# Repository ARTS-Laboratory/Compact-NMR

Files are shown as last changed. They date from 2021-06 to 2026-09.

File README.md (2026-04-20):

# Compact-NMR (cNMR)

A compact Time-Domain Nuclear Magnetic Resonance (TD-NMR) system. The system is made up of custom NMR electronics with a compact and rugged permanent magnet array designed to enable future deployment as an in situ sensor. A signal-to-noise ratio of 25 dB has been demonstrated for a single scan, and sufficient data can be acquired in one minute for Time-Domain measurements. A high-level overview of the system is presented in Figures 1-5. For more details related to its potential use, refer to references [1] and [2]. 

<p align="center">
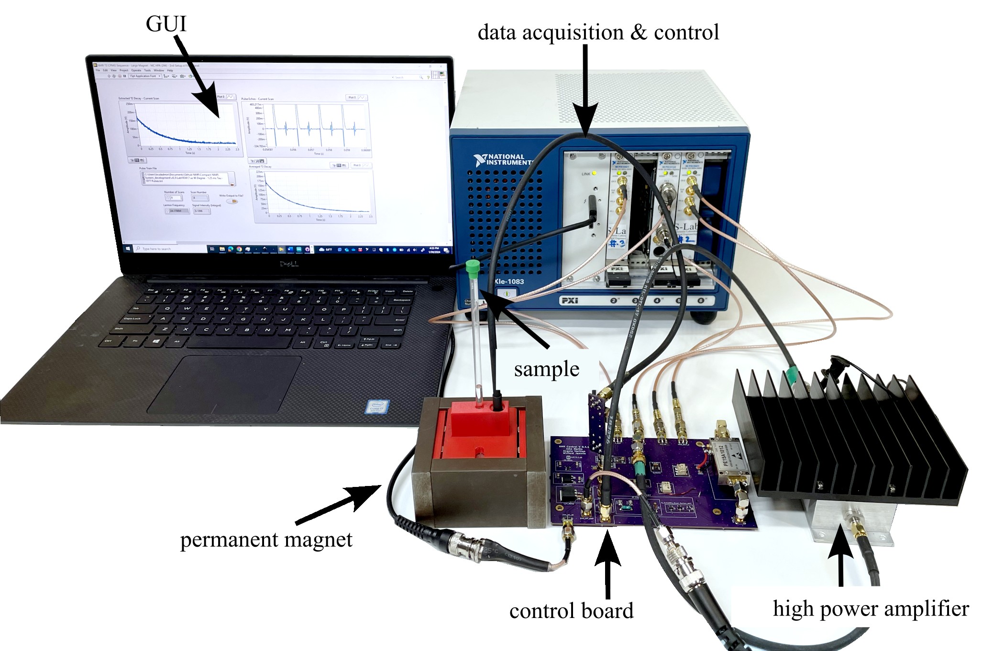
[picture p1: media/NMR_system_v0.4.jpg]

</p>
<p align="center">
Figure 1: Full setup for the TD-NMR system, with key components and subsystems annotated. 
</p>

<p align="center">
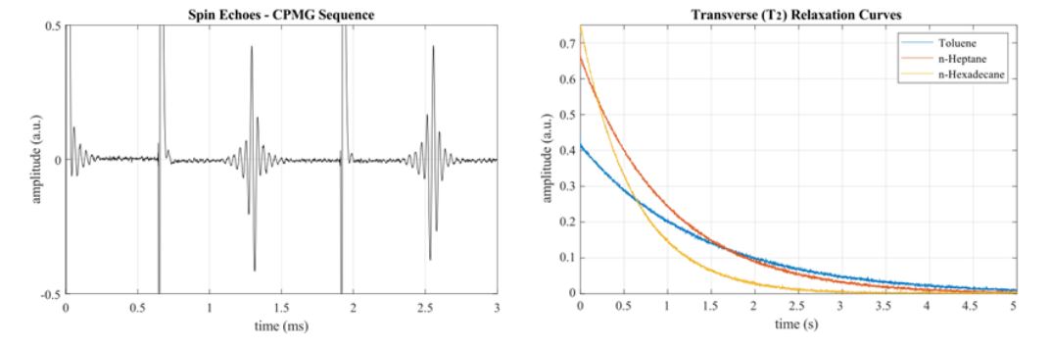
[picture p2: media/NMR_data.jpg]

</p>
<p align="center">
Figure 2: Data Obtained From the Nmr System Showing: (Left) Toluene Spin Echos Resulting From the Application of One 90◦ Pulse and Two 180◦ Pulses, and; (Right) T2 Relaxation Curves for Toluene, Heptane, and Hexadecane Following 32 Averages of 3965 Spin Echo Pulses.  
</p>

<p align="center">
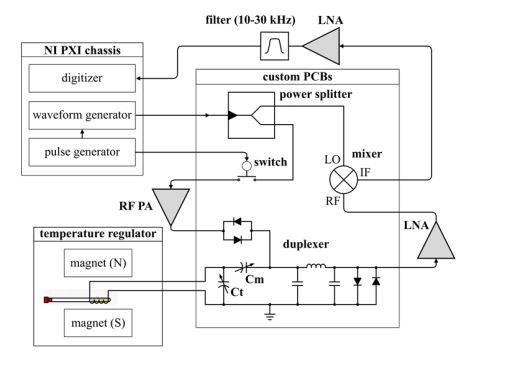
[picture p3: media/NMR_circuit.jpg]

</p>
<p align="center">
Figure 3: Full Schematic of the Control System, Permanent Magnet, and Signal Routing and Amplification Electronics for the Compact Td-nmr System.
</p>

<p align="center">
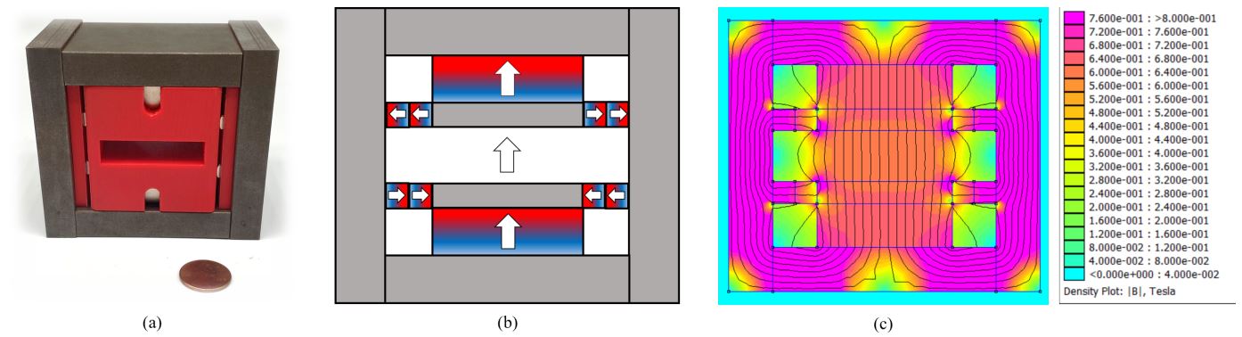
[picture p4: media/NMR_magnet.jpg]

</p>
<p align="center">
Figure 4: The magnet array, showing: (a) fully assembled magnet; (b) orientation of individual magnets and steel pieces, and; (c) two-dimensional finite element simulation.
</p>

<p align="center">
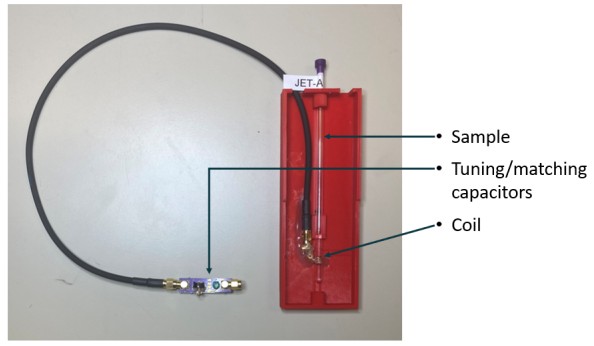
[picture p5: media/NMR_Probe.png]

</p>
<p align="center">
Figure 5: NMR probe with key components annotated. 
</p>

### References
[1] Jacob S. Martin, Austin R.J. Downey, Mohammed Baalousha, and Sang Hee Won. Rapid measurement of magnetic particle concentrations in wildland-urban interface fire ashes and runoff using compact NMR. IEEE Sensors Journal, pages 1-1, 2023. doi:10.1109/jsen.2023.3272882

[2] Jacob Martin, Austin R.J. Downey, and Sang Hee Won. Compact time domain NMR design for the determination of hydrogen content in gas turbine fuels. In Volume 1: 24th International Conference on Advanced Vehicle Technologies (AVT). American Society of Mechanical Engineers, aug 2022. doi:10.1115/detc2022-90023

## [System Development](System_development)
This directory contains the system design files for multiple versions of the compact NMR.

## [Literature](literature)
This directory contains links to important source information for the compact NMR system.

## Licensing and Citation

This work is licensed under a Creative Commons Attribution-ShareAlike 4.0 International License [cc-by-sa 4.0].



Cite this data as: 

#### Bibtex

@Misc{ARTSLabCompactNmr,    
  author = {ARTS-Lab},  
  howpublished = {GitHub},  
  title  = {Compact-{NMR}},  
  groups = {ARTS-Lab},    
  url    = {https://github.com/ARTS-Laboratory/Compact-NMR},   
  note  = {Accessed: Month dd, yyyy},   
}

<p align="center">
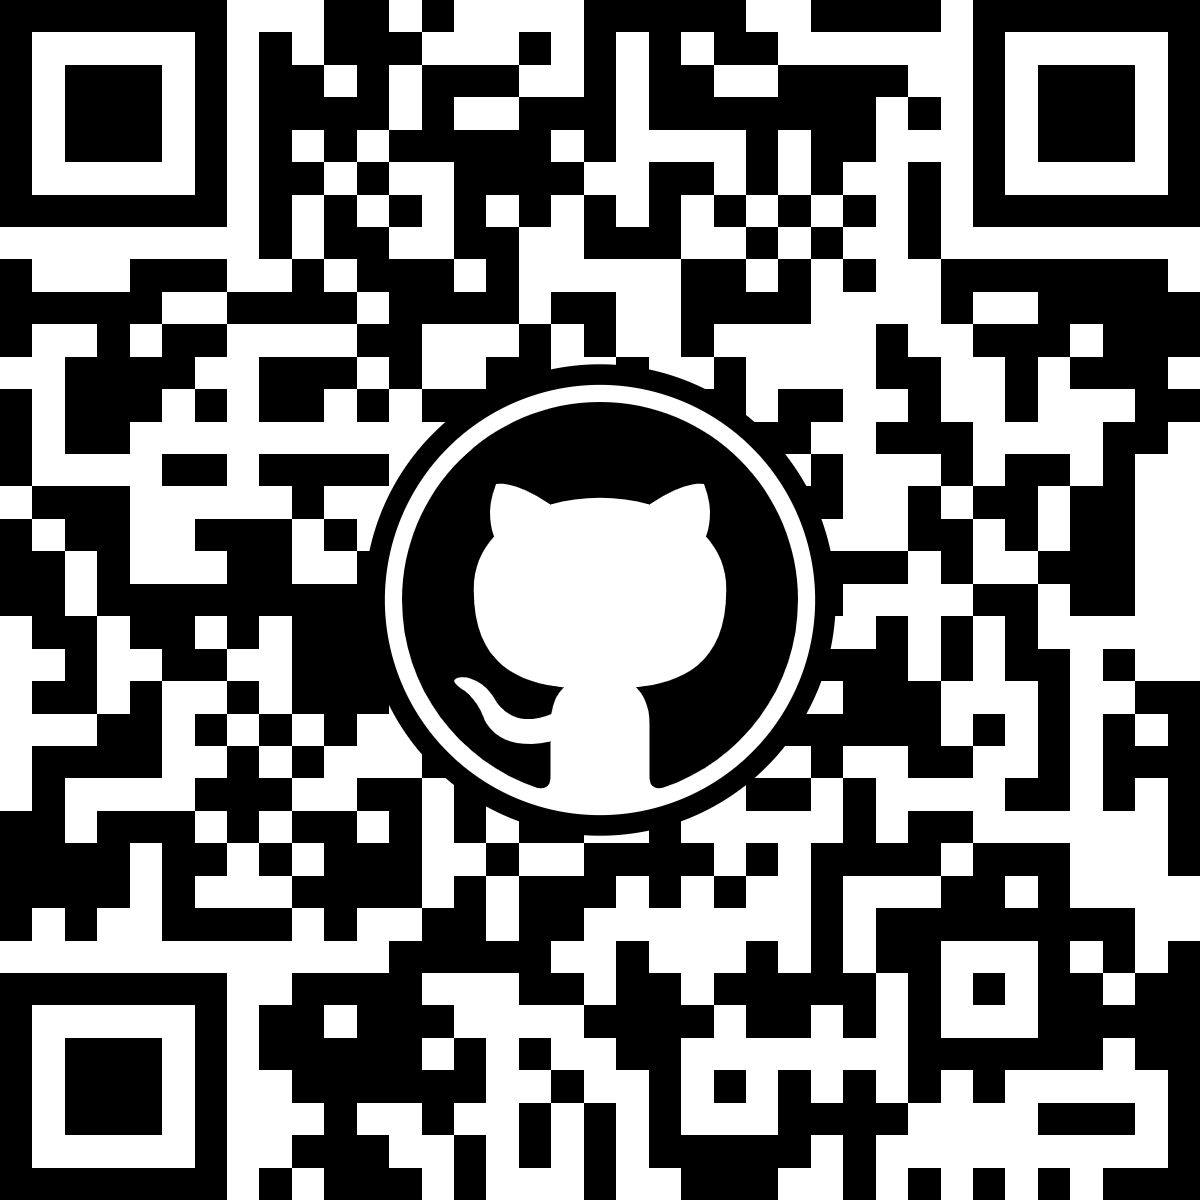
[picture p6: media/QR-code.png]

</p>
<p align="center">
QR code for repo.
</p>

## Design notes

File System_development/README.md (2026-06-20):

# Compact-NMR (cNMR) - System Development 
Various developed systems, named after physicists who worked on aspects related to NMR.

## Van Hove
* A single control board that includes duplexer, voltage regulator, and amplifier on one control board.

<p align="center">

</p>
<p align="center">
The compact NMR system.
</p>

## Dirac
* A small and compact design intended for use in a sensor package design that can be easily deployed and retrieved.

<p align="center">
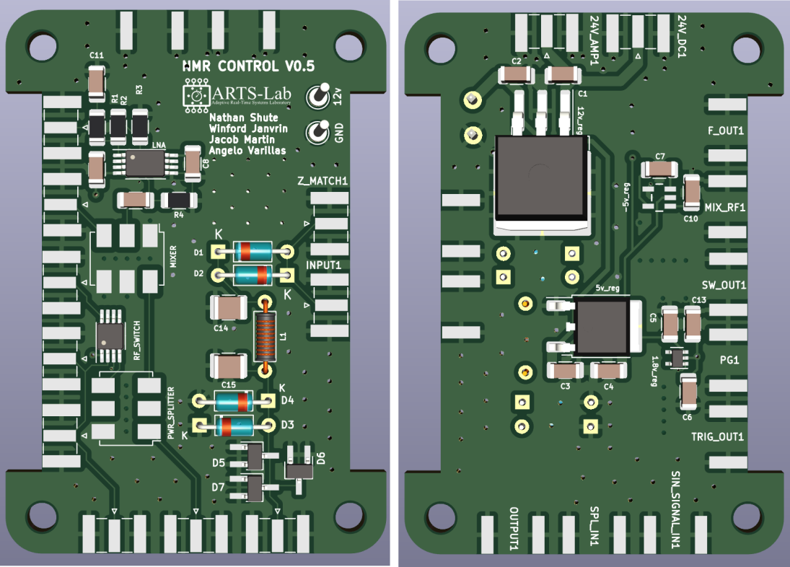
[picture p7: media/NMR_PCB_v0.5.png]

</p>
<p align="center">
The compact NMR system.
</p>

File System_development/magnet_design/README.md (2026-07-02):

# Magnet Design

Designs for Magents following the nomenclature of:
* Letter - the style of the magnet
* Number - the nominal strength of the magnet in milliTesla (rounded to 10 milliTesla)
* Number - the nominal weight of the magnet in hunderds of grams 

For example, A650-10 is a magnet of design "A" with a nominal field strength of 650 milliTesla and an overall weight of 10 kg. The magnet designs are:
  * A - a dual permanent magnet arrangement with a 1018 steel yoke.
  * B - a 10-permanent magnet arrangement consisting of 2 primary magnets and 8 alignment magnets.

## [A320-53 Magnet](A320-53)

## [A500-74 Magnet](A500-74)

## [A650-88 Magnet](A650-88)

## [A650-290 Magnet](A650-290)

## [B300-20 Magnet](B300-20)

## [B570-20 Magnet](B570-20)

* This project uses Inventor 2025 for CAD work

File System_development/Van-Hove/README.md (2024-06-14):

# Compact-NMR (cNMR) - Van Hove

Main aspects of this version are:
* Stable version with all components moved onto one control board that includes duplexer, voltage regulator, and amplifier on one control board.
* A single large PCB measuring approximately 90 x 140 mm.
 
<p align="center">

</p>
<p align="center">
The compact NMR system.
</p>

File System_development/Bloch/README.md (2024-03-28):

# Compact-NMR (cNMR) - v0.2 - Bloch

Main aspects of this version are:
* Most large RF components are replaced with PCB mounted versions.
* The goal is to have the RF signal routing and amplification electronics on one PCB.
* Temperature regulation was added to help increase the magnet stability (which affects testing stability).
* Only one 24V power supply is needed - PCB mounted linear regulators are used to step it down
* Another goal is to get signal generation and data acquisition compacted to on or more PCBs. 
 
<p align="center">
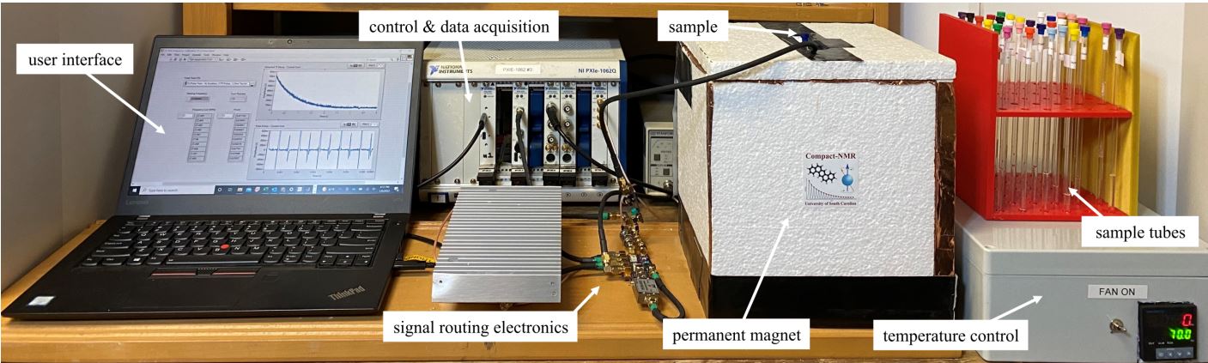
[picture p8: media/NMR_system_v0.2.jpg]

</p>
<p align="center">
The compact NMR system.
</p>

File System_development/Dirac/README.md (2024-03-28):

# Compact-NMR (cNMR) - v0.5 - Dirac

Main aspects of this version are:
* Compact control board designed with size weight and power (SWaP) constraints.
* A single large PCB measuring approximately 40 x 60 mm.
 
<p align="center">

</p>
<p align="center">
The compact NMR system.
</p>

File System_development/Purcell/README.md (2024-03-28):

# Compact-NMR (cNMR) - v0.3 - Purcell

Main aspects of this version are:
* The goal is to further compact the system for in situ measurements/monitoring.
* All routing components are PCB mounted - RF power amplifier and RF LNA are small blocks with SMA ports.
* Want to replace PXI cards with embedded/portable signal generator and data acquisition devices
* Reduced permanent magnet size 

<p align="center">
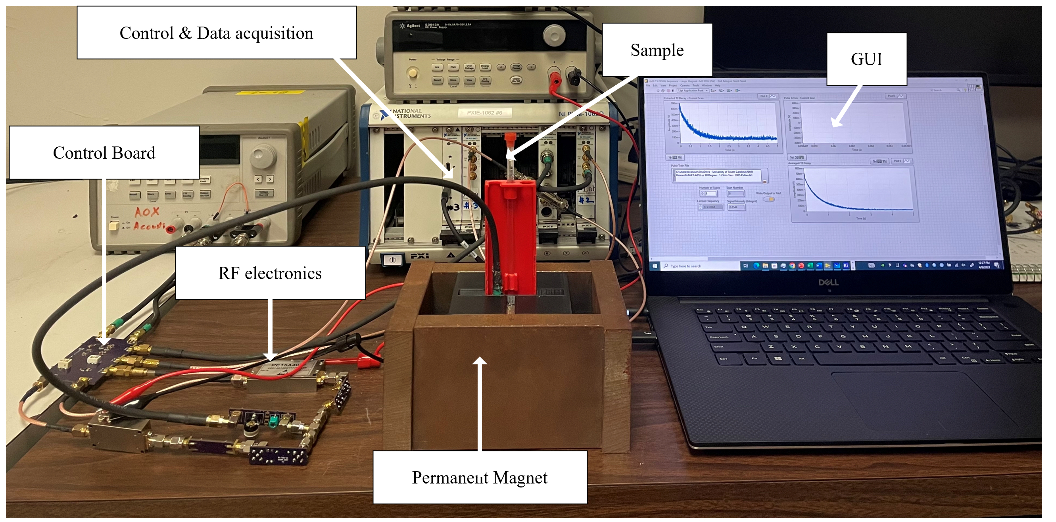
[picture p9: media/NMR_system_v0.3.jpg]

</p>
<p align="center">
The compact NMR system.
</p>

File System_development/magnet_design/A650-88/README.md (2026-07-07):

# A650-88 Tesla Magnet

| Magnet Type | Size                        | Price      | Weight    | Magnetic Field Strength |  
| ----------- | --------------------------- | ---------- | --------- | ----------------------- | 
|      A      | 3 Inch (Diameter) x 1 Inch  |   $207.71  |  56.8 lbs |        0.65 Tesla       | 

## Magnet design, simulation, and product
The permanent magnet assembly uses:
* DZ0X0-N42: https://www.kjmagnetics.com/dz0x0-neodymium-disc-magnet

<div align="center">

  <figure>
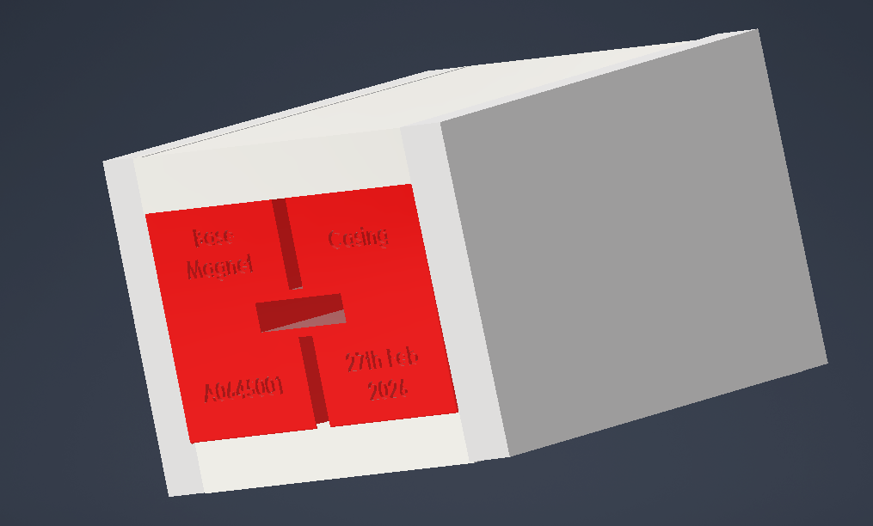
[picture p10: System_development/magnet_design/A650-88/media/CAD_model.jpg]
CAD model of the magnet design
     <br>
    <figcaption><strong>CAD model:</strong> 3D CAD rendering of the permanent magnet assembly.</figcaption>
  </figure>

  <br>

  <figure>
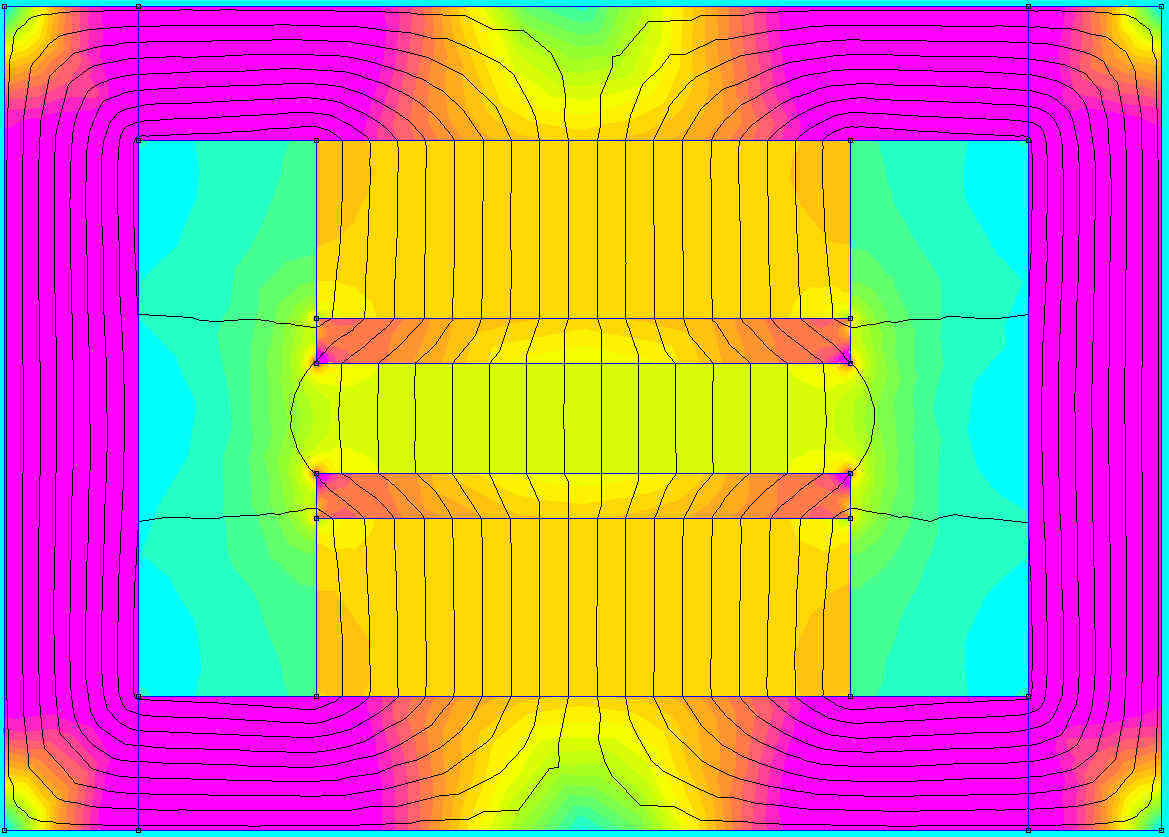
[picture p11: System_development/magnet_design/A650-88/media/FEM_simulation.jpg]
2D finite element magnetic model and simulation
     <br>
    <figcaption><strong>Finite element simulation:</strong> 2D magnetic field model used to evaluate the magnet assembly design.</figcaption>
  </figure>

  <br>

  <figure>
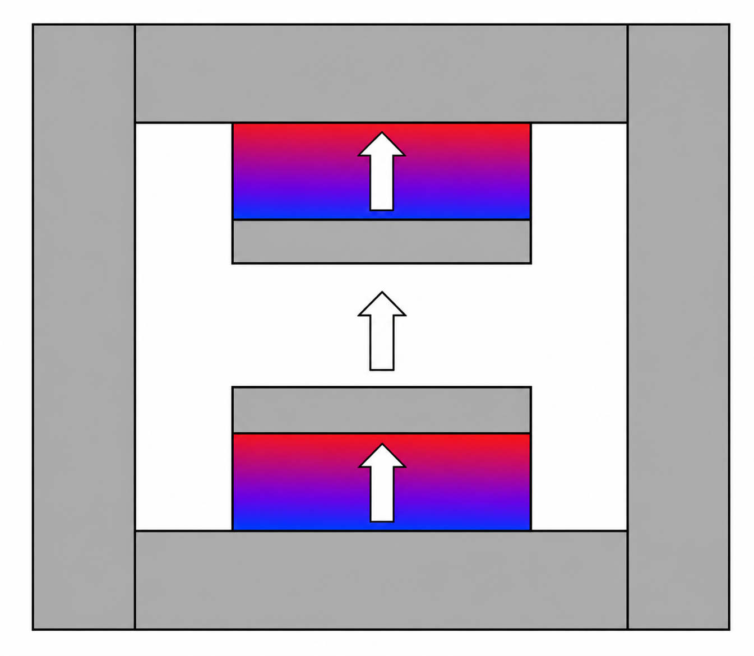
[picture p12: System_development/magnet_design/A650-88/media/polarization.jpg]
Polarization plot of the magnet
     <br>
    <figcaption><strong>Polarization plot:</strong> Magnet polarization layout showing the orientation of the magnetic elements.</figcaption>
  </figure>

  <br>

  <figure>
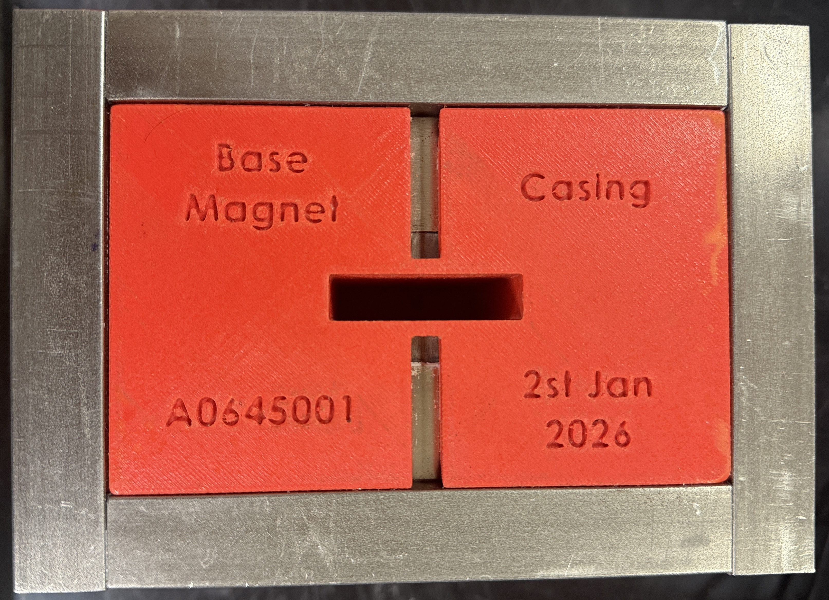
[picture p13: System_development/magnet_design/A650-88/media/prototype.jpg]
Assembled magnet prototype
     <br>
    <figcaption><strong>Prototype:</strong> Assembled physical magnet prototype.</figcaption>
  </figure>

  <br>

  <figure>
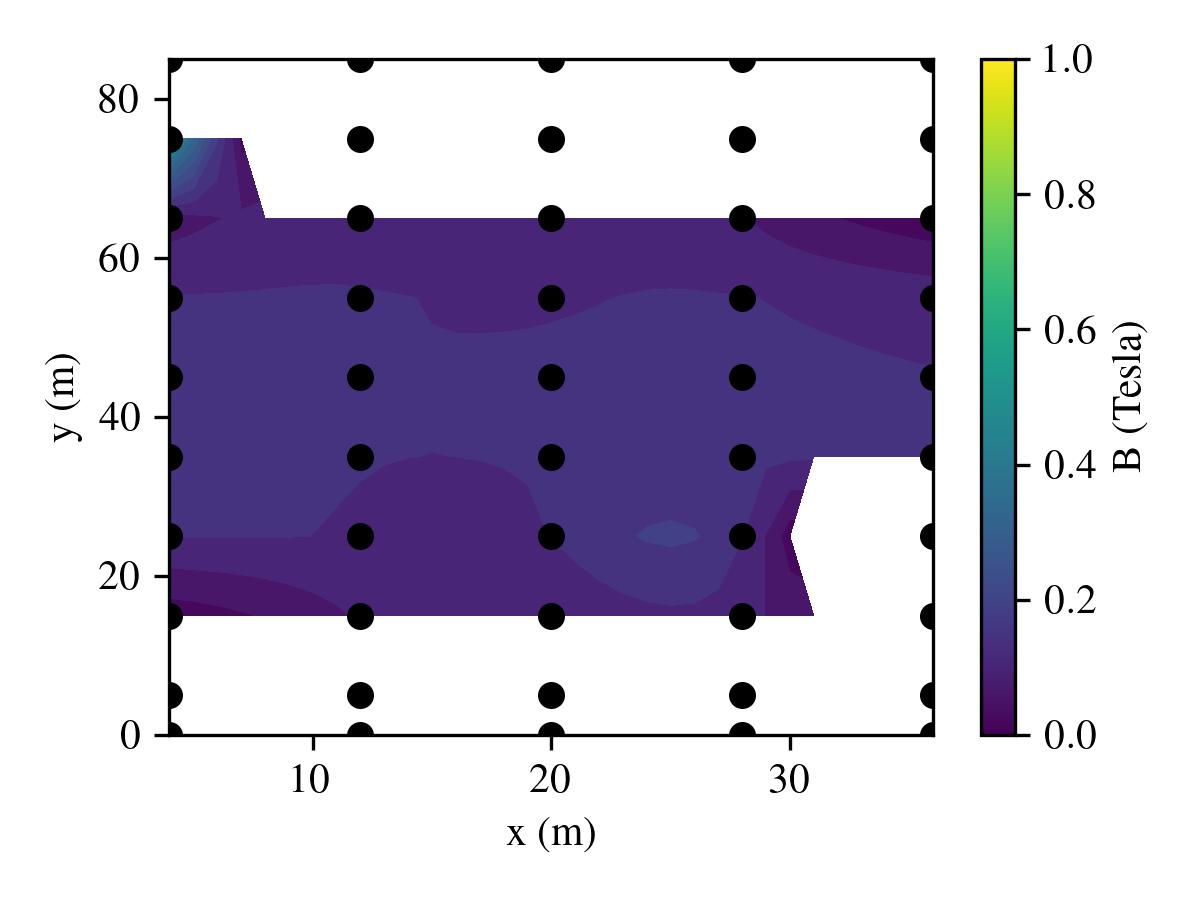
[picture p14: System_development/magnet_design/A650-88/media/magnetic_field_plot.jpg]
Measured magnetic field plot
     <br>
    <figcaption><strong>Magnetic field map:</strong> Measured magnetic field distribution across the magnet region.</figcaption>
  </figure>

  <br>
  
  <figure>
    Full vertical case, magnet, and tray assembly <br>
    <figcaption><strong>Vertical assembly:</strong> Full vertical case, magnet, and tray assembly.</figcaption>
  </figure>

  <br>

  <figure>
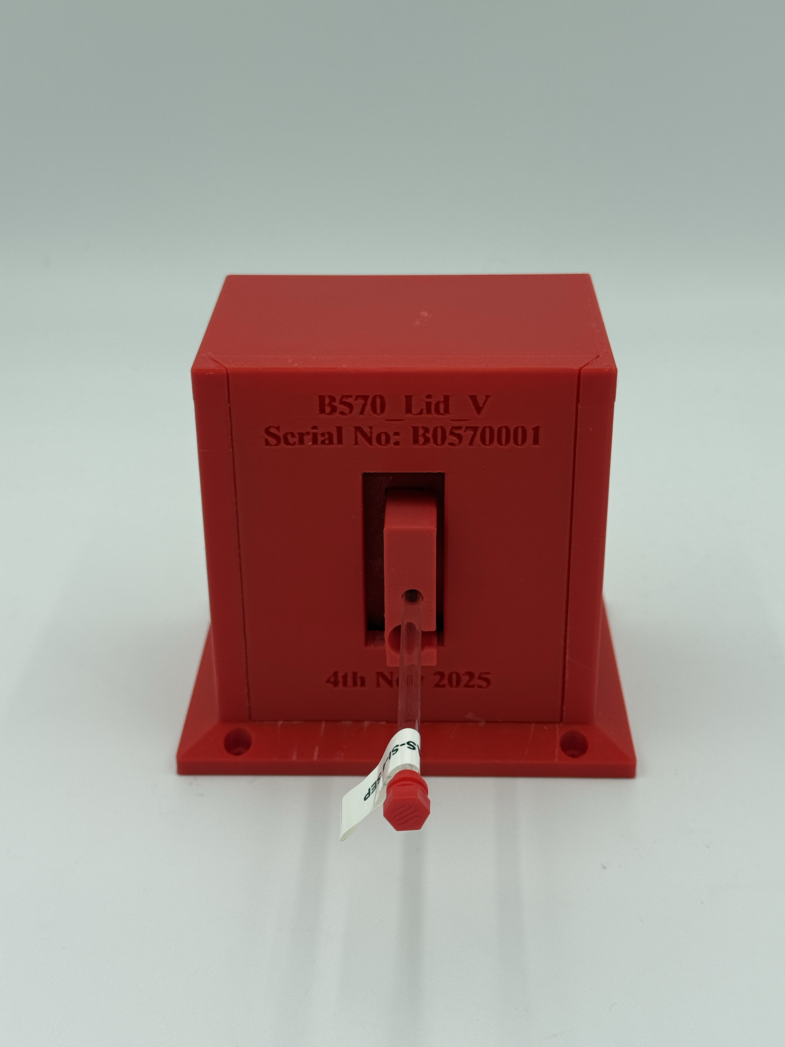
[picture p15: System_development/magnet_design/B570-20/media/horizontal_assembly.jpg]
Full horizontal case, magnet, and tray assembly
     <br>
    <figcaption><strong>Horizontal assembly:</strong> Full horizontal case, magnet, and tray assembly.</figcaption>
  </figure>

</div>

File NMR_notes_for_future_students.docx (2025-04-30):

NMR Notes for Future Students

Chapters:

1 – Setting up, extracting signal, and maximizing signal

2 – Running the LabVIEW

3 – Future Work

Chapter 1

Setting Up

When connecting the main PCB to the PXI chassis, power supply, and amplifier, be sure that all cords are properly connected. After completing setup, if you do not see the pulses (near vertical lines that go to 1.3V), then cords are not properly connected. It is possible that if this happens, there is something wrong with the PCB. Only check this if you have modified the PCB in some way or exhausted all other options, but in this case, it can be helpful to resolder all components in the duplexer, being sure to not leave much extra solder paste. You can also look at the calibration on the pi filter in this case.

If the power supply doesn’t read 24V, ~1A be sure that you are on the right channel and the channel is set to be able to supply 24V, ~1A. If it is set up correctly and that is not occurring, there is a short somewhere. That can either be due to bad connection (disconnect and reconnect all wires) or a blown component on the PCB (good luck).

Finding Signal

Once you see the pulses, then you can start finding the signal. First, be sure that there is a sample in the magnet and that the coil is encompassing the sample – if that is not the case, you won’t see any signal. For the large magnet, start at 27.6 MHz and for the small magnet start at 24.2 MHz. You will want to check frequencies above this if it is cold and frequencies below this if it is warm. Start by going up/down by 0.01 or 0.02 MHz. As long as you are in somewhat normal temperature ranges, you should see signal by +/- 0.15 MHz from the start. If you start to see spin echoes inbetween the pulses then you can move on to maximizing signal. If you go through that range both above and below the starting point, there are some steps you can take.

First, double check that your coil is set up properly and is in the middle of the coil PCB. Check that the solder pads are not bent or twisted any way. Ensure that the coil is encompassing your sample. Ensure that your sample is in the strongest point of the magnet (usually this will be the center of the magnet, but for the large magnet this is not the case, there is a faint sharpie mark on the tray). If all else fails, you need to calibrate the impedance matching board. When doing this, it is vital to use the same cord and coil that you use for measurement (more info on this is in the HardwareX paper). If after all of these steps, you can’t find a signal, step away and do something else for a little bit – you probably did something wrong. If you are working with a new PCB, the pi-filter calibration capacitors might be wrong or you are using the wrong PCB with the wrong magnet.

Maximizing Signal

Maximizing signal can be pretty tough. Jake was able to achieve >400mV consistently. The hardware the group used between Jake leaving and myself arriving changed and ever since I have been here, 250mV has been considered good. I have tried to figure out what happened between his departure and my arrival that caused this dip, but to no avail. I have ruled out amplifiers, filters, general troubleshooting, and PCB components.

Things that Mess up Signal

If the magnet is too close to ferromagnetic objects or other magnets, it will mess with the homogeneity of the magnet and result in much less signal. Raise the magnet off the desk or put it in our makeshift Faraday cage

Try messing with the orientation of the coil slightly by pushing it up or down a little bit. It should be in-between the two solder pads on the coil PCB, but sometimes pushing it up or down can help achieve better signal

Fine-tune the Larmor frequency to find where signal is maximized

Double checking impedance matching calibration can drastically improve signal quality, this should be done once a week at least, it is a very quick process

Double checking pi filter calibration should only be done if nothing else works, but it can possibly be helpful

Chapter 2

LabVIEW Code

With LabVIEW, there are two different screens you can look at, the front panel and the block diagram. The front panel is used to monitor and adjust the way the code runs while the block diagram houses the code. It is helpful to take some time to understand what everything on the block diagram does. I won’t explain individual functions because I think that is best for you to explore. In general, the LabVIEW code does several things:

1- Creates a sine waveform, a custom pulsed waveform, and an oscilloscope instance
2- Uses the oscilloscope to collect data
3- Find peaks (spin echoes) – this process is done pretty inefficiently and goes through the dataset index by index for each spin echo to find the local maxima of a subset of indices
4- Take those peaks and place them into an array that then gets plotted on the front panel for the current scan
5- 1-4 are repeated for each scan
6- The average of the peaks are taken and stored into an array, plotted on the front panel, and saved as a csv file

Running the LabVIEW

In order to use LabVIEW, there are a few things you need to do:

- Be sure that the pulse file on the front panel is the one you want
- Be sure that the “Write output to file” button is on/off as needed
- Update the Larmor Frequency and the number of scans as needed

After these steps, the front panel is ready. There are also a few things you need to do on the block diagram:

- Depending on the specific iteration of the code, you may need to specify where the file is being saved

Now, the code is ready to be ran. There are a few issues that may arise. If you don’t see a nice decay curve, check to be sure you are using the pulse sequence and the LabVIEW code that you need to be using. If you change pulse sequences, you will need to change the indices of the peak-finding algorithm.

Additionally, if you run into an error of the oscilloscope not finding data, you can either go to the PXI chassis and exchange the sine waveform connections and the pulse waveform connections, or you can go into the block diagram and switch which device is connected to the sine waveform and the pulse waveform. Just swap them with each other. This may need to be repeated twice because on semi-rare occasions, it doesn’t work properly. This error is caused by the switch on the main PCB never switching due to it receiving the sine waveform rather than the pulse waveform. After fixing that, the code should run just fine

Chapter 3

There are several long-term goals of NMR that will need to be explored soon. In my thesis, we only looked at using copper contaminated water and utilizing an ML model on that copper data to predict the amount of copper in creeks. In reality, there will be multiple contaminants in creek water at any given time. There are a few ways this problem can be approached:

- Train the ML model on various types of contaminants. Since each contaminant will have a different magnetic moment, different amounts of different contaminants will affect the relationship between T2 time and contaminant concentration differently. Each contaminant will have a linear relationship between 1/T2, but the coefficient for that relationship will vary. Because of this, 1/T2 is a function of multiple different lines. This can be looked at with ML or mathematically. 1/T2 = mx + nz kind of equation would describe this where m and n are slopes and x and z are different contaminant concentrations
- Instead of using single exponential fitting to create a fitted T2 curve, resulting in a T2 time, look at using multiple exponential fits (sum of more than one exponential). Since we have multiple contaminants, this should able to create an exponential for each contaminant. This will allow us to distinguish contaminants.
- See how these ideas can compliment each other. We aren’t looking at different substances containing Hydrogen – we are just looking at how different paramagnetic materials can affect the NMR response of Hydrogen, it is possible that the multi-exponential fit might not be very helpful. However, even if it doesn’t provide an answer on its own, it could still provide parameters for an ML model and could be useful and combined into the first idea here.

Another long-term idea is the introduction of ligands to our system. Since we are limited to looking at Hydrogen and paramagnetic materials that affect Hydrogen compounds, there are only so many things we can measure. The idea of a ligand is to introduce a foreign compound containing Hydrogen that can be used to bond with other contaminants. This will give us a way to measure things we couldn’t measure otherwise. Additionally, these ligands are often designed to only bond for short periods of time, so they will eventually un-bond and allow us to separate out the ligand again. Implementing this in a flow-through system would be quite difficult, but it is something to consider in the future. The previous idea of distinguishing multiple contaminants is much more important than this idea, however.

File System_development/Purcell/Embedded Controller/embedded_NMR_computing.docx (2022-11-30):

# In Situ NMR Project Specifications

# Embedded Computing

The embedded computing will generate the high-frequency excitation signal and process the received signal. This will include embedded machine learning for classification and wireless data transfer. Energy consumption and ease of modification\updating of both hardware and software are of high importance.

#### Excitation Signal Generation

- Operate up to 30 MHz with a bandwidth of 30 MHZ @ 1 dB
- Start at the same phase (preferably 0 for sine wave) every time it’s triggered
- Have a minimum adjustment of 1 kHz (i.e. 24.001 MHz, 24.002 MHz…)
- Update speed of 100 MS/s
- Output range: ±1V
- Resolution: 10-bit precision (5 mv on a ±3V signal)

#### Data Acquisition

- Channels: 1
- Channel type: single-ended
- Input range: ±1V
- Resolution: 10-bit (1.9 mV on a ±1V signal)
- Sample rate 100 kS/s (for a ~10 kHz NMR signal)
- Input impedance: 1MΩ and less than 20pF
- Analog bandwidth: 1010-40: 20 MHz @ 3dB, 8 MHz @ 0.5dB, 4 MHz @ 0.1dB
- Input protected to: ±50V

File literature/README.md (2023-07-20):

# Literature
Literature that was fundamental in the development of the cNMR system. 

1. Pulsed NMR Lab (Berkeley)
    + This is not a paper, but it is a lab at Berkeley where they investigate pulsed and continuous NMR. It does a great job of showing the details of the schematic and setup, as well as explain a lot of the theory behind it. 
    + http://experimentationlab.berkeley.edu/PulsedNMR#Sample_Coil
1. Louis-Joseph, Alain, and Philippe Lesot. "Designing and building a low-cost portable FT-NMR spectrometer in 2019: A modern challenge." Comptes Rendus Chimie 22.9-10 (2019): 695-711.
    + This paper is about how a French group designed and built a benchtop NMR spectrometer. It is super helpful and explains the steps that they took as well as all of the specific equipment used. The data, however, is not presented very well and is a bit hard to view. 
    + “In this article, we describe the realization of an NMR instrument based on electronic components and boards (LNA, ADC, FPGA, ARM, DDS…) easily commercially available”
    + https://www.sciencedirect.com/science/article/pii/S1631074819301055
1. Moresi, Giorgio, and Richard Magin. "Miniature permanent magnet for table‐top NMR." Concepts in Magnetic Resonance Part B: Magnetic Resonance Engineering: An Educational Journal 19.1 (2003): 35-43.
    +	This is another decent paper on how a miniature NMR experiment was set up and tested but using a Halbach magnet design rather than two pancake type magnets. Given the design and the fact that there isn’t a lot of amplification or separation from probe/acquisition, I don’t really understand how they actually got it to work. Nonetheless, it’s a good example of a possible mini-NMR setup. 
    +	“A simple NMR relaxation time experiment was performed on a water sample doped with 40 mM of CuSO4. This system in its current configuration is suitable for relaxation time studies of materials or for educational use. The introduction of shim coils would increase the homogeneity of the magnet by a factor of 100, allowing the system to be used as a portable NMR spectrometer.”
    +	https://onlinelibrary.wiley.com/doi/pdf/10.1002/cmr.b.10082
1. ASTM D7171. "Standard Test Method for Hydrogen Content of Middle Distillate Petroleum Products by Low‐Resolution Pulsed Nuclear Magnetic Resonance Spectroscopy." (2020).
1. ASTM D4808. "Standard Test Methods for Hydrogen Content of Light Distillates, Middle Distillates, Gas Oils, and Residua by Low-Resolution Nuclear Magnetic Resonance Spectroscopy." (2017).
1. ASTM D3701. "Standard Test Method for Hydrogen Content of Aviation Turbine Fuels by Low Resolution Nuclear Magnetic Resonance Spectrometry." (2017).

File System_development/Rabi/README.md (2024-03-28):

# Compact-NMR (cNMR) - v0.1 - Rabi

Main aspects of this version are:
* The circuitry included large RF components with SMA connections.
* The initial static magnetic field was generated using two bare, cylindrical N42 magnets.
* RF signal generation, square pulse generation, and data acquisition is controlled by an NI PXI chassis.
* The magnet design was later upgraded with carbon steel bars to be stronger and more homogenous.  

<p align="center">
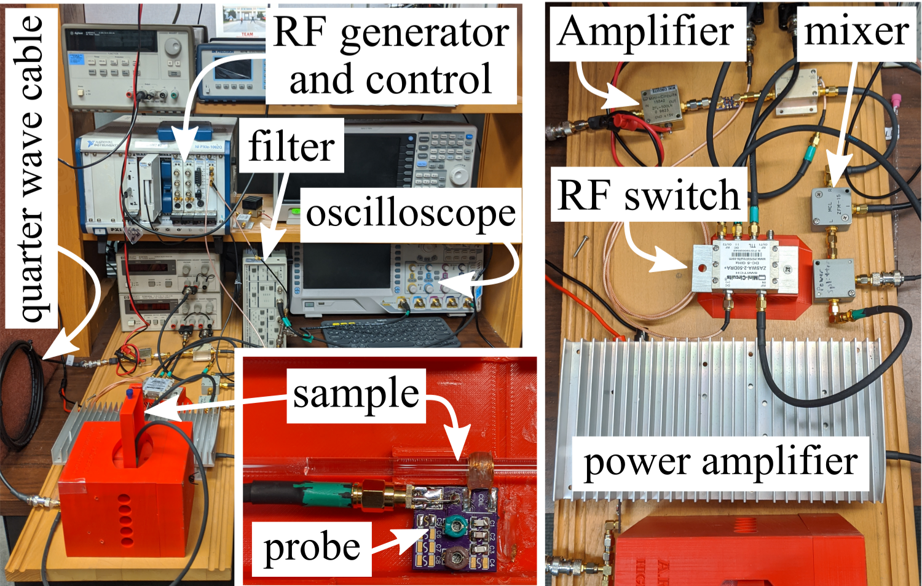
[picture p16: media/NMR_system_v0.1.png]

</p>
<p align="center">
The compact NMR system.
</p>

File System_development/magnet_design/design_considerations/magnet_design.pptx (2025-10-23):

## Magnet Design Considerations for Compact NMR

## Why Develop a Homogenous Magnetic Field?

- Higher homogeneity → sharper signals but reduced bandwidth and robustness in field conditions

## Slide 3

## Magnet Simulations

## …

- …

## …

- …

## Magnet Type A

## …

- …

## …

- …

## Magnet Type B

## …

- …

## …

- …

## Thank You for Your Time

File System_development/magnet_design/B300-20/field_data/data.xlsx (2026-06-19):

x/y | 4 | 12 | 20 | 28 | 36
0 | 1133 | 1369 | 1420 | 1380 | 1184
10 | 2322 | 2779 | 2814 | 2790 | 2576
20 | 2514 | 2929 | 2954 | 2936 | 2730
30 | 2512 | 2920 | 2940 | 2925 | 2671
40 | 2300 | 2663 | 2695 | 2673 | 2436
50 | 1070 | 1340 | 1335 | 1311 | 1100

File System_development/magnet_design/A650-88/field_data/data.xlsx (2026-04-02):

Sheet: A645
x/y | 4 | 12 | 20 | 28 | 36
0 | 2685 | 3184 | 3309 | 3072 | 2611
5 | 4913 | 5374 | 5686 | 5572 | 4801
15 | 6315 | 6414 | 6428 | 6426 | 6349
25 | 6468 | 6460 | 6466 | 6467 | 5460
35 | 6483 | 6467 | 6473 | 6477 | 6470
45 | 6486 | 6468 | 6475 | 6472 | 6468
55 | 6468 | 6469 | 6460 | 6466 | 6442
65 | 6378 | 6436 | 6440 | 6410 | 6307
75 | 6989 | 5763 | 5955 | 5570 | 4820
85 | 2130 | 2870 | 3100 | 2816 | 2050

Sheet: B295
x/y | 4 | 12 | 20 | 28 | 36
0 | 1133 | 1369 | 1420 | 1380 | 1184
10 | 2322 | 2779 | 2814 | 2790 | 2576
20 | 2514 | 2929 | 2954 | 2936 | 2730
30 | 2512 | 2920 | 2940 | 2925 | 2671
40 | 2300 | 2663 | 2695 | 2673 | 2436
50 | 1070 | 1340 | 1335 | 1311 | 1100

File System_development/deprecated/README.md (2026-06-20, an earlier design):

# Deprecated Variations of the Compact-NMR (cNMR) 
Various developed systems, named after physicists who worked on aspects related to NMR.

## Rabi
* A full-scale development system that uses full-size amplifiers, filters, and switches. 

<p align="center">

</p>
<p align="center">
The compact NMR system.
</p>

## Bloch
* A full-scale development that combines amplifiers, filters, and switches onto custom PCB boards.

<p align="center">

</p>
<p align="center">
The compact NMR system.
</p>

## Purcell
* A design with temperature regulation removed in favor of a frequency calibration method.

<p align="center">

</p>
<p align="center">
The compact NMR system.
</p>

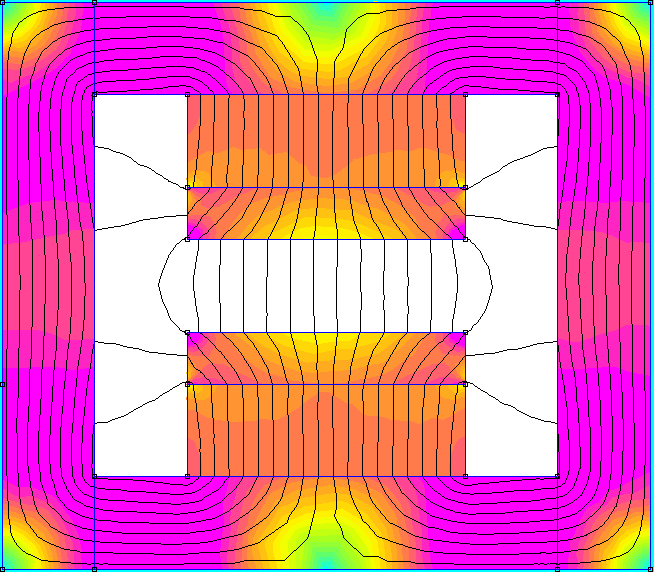
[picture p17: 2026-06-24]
System_development/magnet_design/A500-74/media/FEM_simulation.jpg

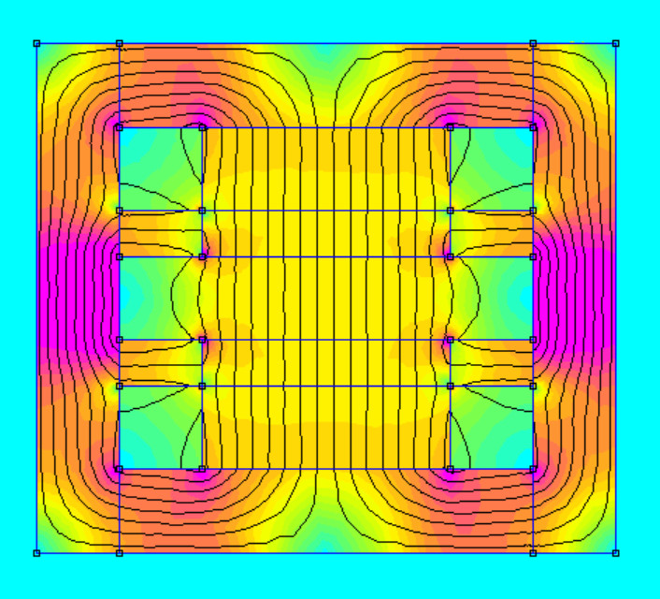
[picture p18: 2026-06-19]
System_development/magnet_design/B300-20/media/FEM_simulation.jpg

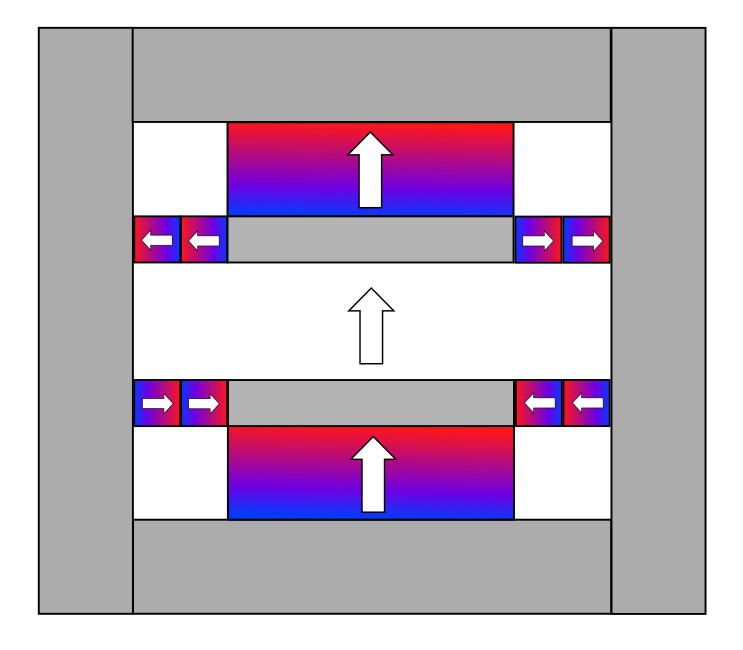
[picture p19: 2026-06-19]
System_development/magnet_design/B570-20/media/polarization.jpg

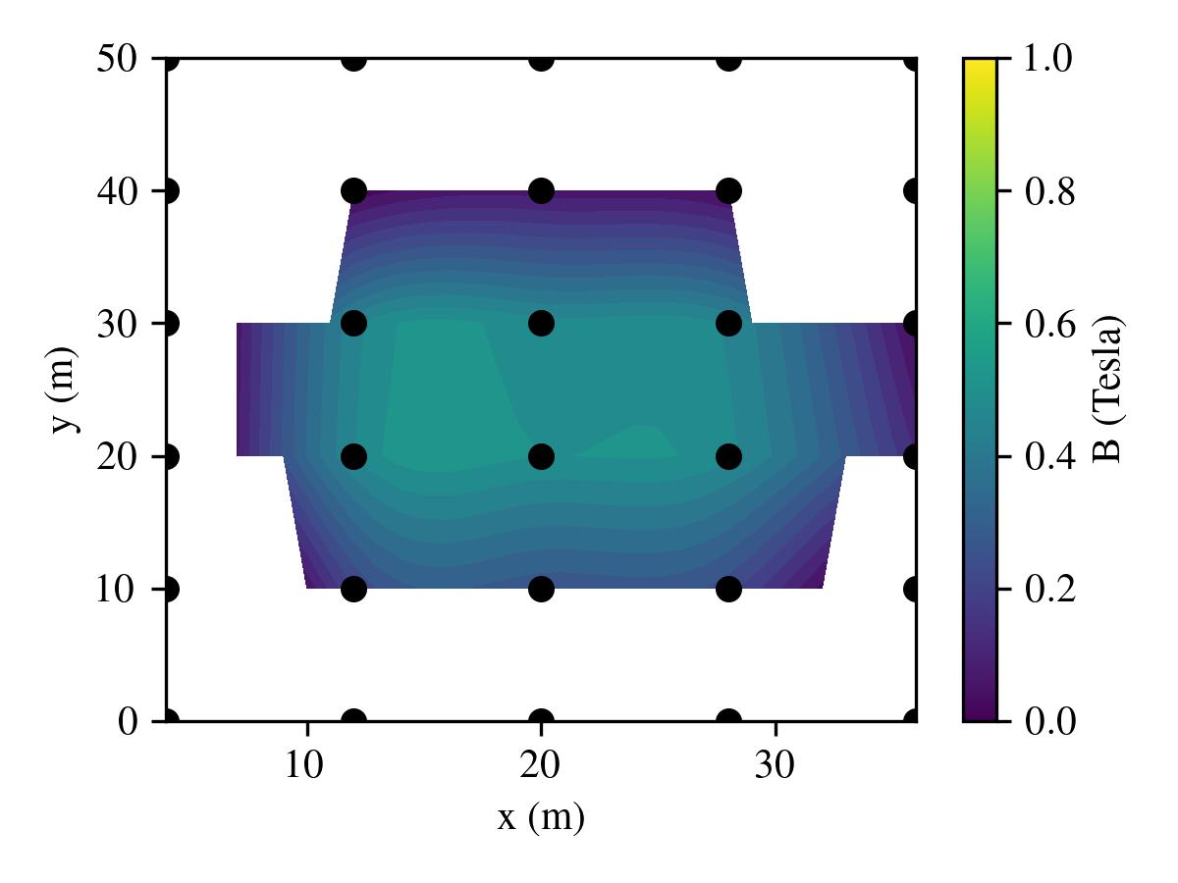
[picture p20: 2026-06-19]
System_development/magnet_design/B300-20/media/magnetic_field_plot.jpg

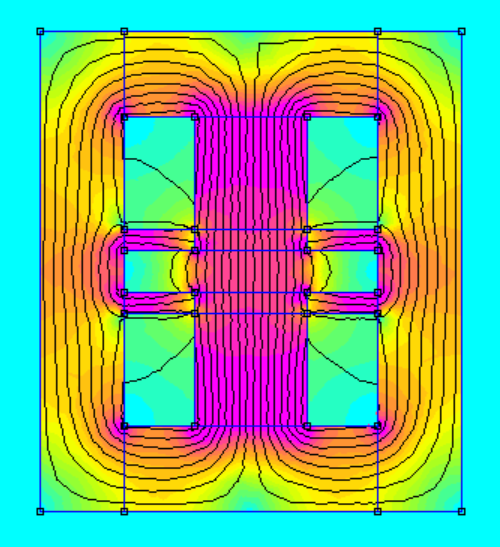
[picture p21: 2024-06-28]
System_development/magnet_design/B645_Tesla_magnet/media/Simulation_Magnet.PNG

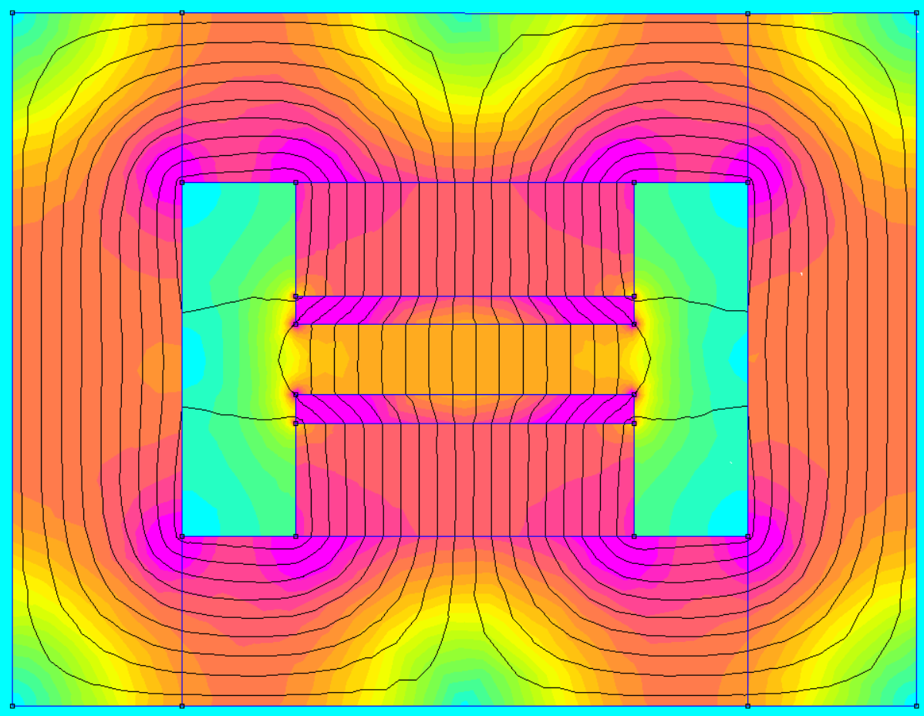
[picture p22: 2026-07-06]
System_development/magnet_design/A650-290/media/FEM_simulation.jpg

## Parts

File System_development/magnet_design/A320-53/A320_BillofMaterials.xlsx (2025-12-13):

BILL OF MATERIALS
Designator | Component | Amount | Individual Cost | Total Cost | Vendor 1 | Vendor 2 | Vendor 3 | Vendor 4
Iron Yoke | Carbon Steel Rectangular Bar: 1018, 0.75 in Thick, 3 1/2 in x 36 in Nominal Size (WxL), -0.003 in | 1 | $105.00 | $105.00 | https://www.grainger.com/product/Carbon-Steel-Rectangular-Bar-2HHV2?opr=PLADS&analytics=FM%3APLA&a2c_sku_original=2HHT9&position=3
NN52 square Disc Magnet | 3 x 3 x 1/4 Inch Neodymium Rare Earth Block Magnet N52 | 2 | $95.32 | $190.64 | https://www.kjmagnetics.com/bz0z04-n52-neodymium-block-magnet
Iron Face Plate | Carbon Steel Rectangular Bar: 1018, 0.25 in Thick, 3 in x 12 in Nominal Size (WxL), -0.003 in, Mill | 1 | $17.43 | $17.43 | https://www.grainger.com/product/Carbon-Steel-Rectangular-Bar-2HGZ8

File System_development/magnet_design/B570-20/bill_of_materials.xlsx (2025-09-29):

Designator | Component | Amount | Individual Cost | Total Cost | Vendor 1 | Vendor 2 | Vendor 3 | Vendor 4 | Vendor 5 | Vendor 6
2.54mm JST 3 pin | B3B-XH-A | 1 | 0.13 | 0.13 | https://www.digikey.com/en/products/detail/jst-sales-america-inc/B3B-XH-A/1651046?gad_source=1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 | https://www.ebay.com/itm/135516167050?_skw=B3B-XH-A&itmmeta=01JXJN27KW3SV3ZA95H65390XD
Solar panels | SM141K06TF | 9 | 7.39 | 66.51 | https://www.digikey.com/en/products/detail/anysolar-ltd/SM141K06TF/14311398
M2 nut |  | 2 | 0.01 | 0.02
M2 bolt |  | 2 | 0.073 | 0.14 | https://www.grainger.com/product/Machine-Screws-M2x0-40-Thread-6GY22?
O-Rings |  | 1 | 4.7 | 4.7 | https://www.grainger.com/product/41KX35?RIID=51819294775&GID=729415832&mid=OrderConfirmation_REST&gucid=EMT:11126144:Item:CSM-323&emcid=NA:Item
Total Cost | 71.5

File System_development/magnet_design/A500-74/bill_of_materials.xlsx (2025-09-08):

Designator | Component | Amount | Individual Cost | Total Cost | Vendor 1 | Vendor 2 | Vendor 3 | Vendor 4 | Vendor 5 | Vendor 6
Arduino Nano | Arduino Nano | 1 | 25.7 | 25.7 | https://store-usa.arduino.cc/products/arduino-nano?gad_source=1 | https://www.digikey.com/en/products/detail/arduino/A000005/2638989?gclsrc=aw.ds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 | https://www.ebay.com/itm/254630577493?chn=ps&google_free_listing_action=view_item&gQT=2
Micro SD card slot/tray | 112J-TDAR-R01 | 1 | 2.52 | 2.52 | https://www.digikey.com/en/products/detail/attend-technology/112J-TDAR-R01/17634680 | https://www.ebay.com/itm/235081679206?chn=ps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
NRF24L01+ | NRF24L01+ 2.4GHz Wireless RF Transceiver Module | 1 | 1.4 | 1.4 | https://www.amazon.com/Makerfire-Arduino-NRF24L01-Wireless-Transceiver/dp/B00O9O868G?mcid=dab308f0de3430dfa5c9f8399ca22b35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 | https://www.digikey.com/en/products/detail/ai-thinker/NF-01-S/16688873?gclsrc=aw.ds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 | https://www.ebay.com/itm/185777140664?itmmeta=01JXJF02RJ2SD81DKBZE32WGPJ
DS3231 real-time clock | DS3231M+ | 1 | 11.96 | 11.96 | https://www.digikey.com/en/products/detail/analog-devices-inc-maxim-integrated/DS3231M/2402420 | https://www.mouser.com/ProductDetail/Analog-Devices-Maxim-Integrated/DS3231M%2b?qs=Bakm8ERcljpd4MQpcnSykw%3D%3D
BME280 environmental sensor | BME280 | 1 | 5.26 | 5.26 | https://www.amazon.com/Onyehn-Temperature-Humidity-Barometric-Pressure/dp/B07KR24P6P?mcid=2faf80a473c33e3bb7b53dc75a65a9ac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 | https://www.ebay.com/itm/223602242983?chn=ps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 | https://www.ebay.com/itm/183678893844?chn=ps&google_free_listing_action=view_item&gQT=2
INA219 current sensor | INA219BIDR | 1 | 2.03 | 2.03 | https://www.digikey.com/en/products/detail/texas-instruments/INA219BIDR/2426057?s=N4IgTCBcDaIJIDkCCYCMBOAQnAIgJRAF0BfIA | https://www.mouser.com/ProductDetail/Texas-Instruments/INA219BIDR?qs=1WmUhT/VMINyGsXNJcdD5Q%3D%3D&mgh=1&gQT=2 | https://www.ti.com/product/INA219/part-details/INA219BIDR
N42 permanent magnet | Neodymium Disc Magnet - 1 1/4" Dia x 3/8" Thi | 1 | 15.2 | 15.2 | https://www.kjmagnetics.com/dx46-neodymium-disc-magnet
Ultrasonic sensor | HC-SR04 | 1 | 5.25 | 5.25 | Ultrasonic Distance Sensor - 5V (HC-SR04) (https://www.sparkfun.com/ultrasonic-distance-sensor-hc-sr04.html) | https://www.digikey.com/en/products/detail/adafruit-industries-llc/3942/9658069?gclsrc=aw.ds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 | https://www.ebay.com/itm/192312930293?chn=ps&google_free_listing_action=view_item
2s 7.4V LiPo battery | Zeee 2S Lipo Battery 1500mAh 7.4V 60C with Deans Plug | 1 | 18 | 18 | https://zeeebattery.com/products/zeee-7-4v-60c-1500mah-2s-lipo-battery-deans-plug?variant=43953770299699&country=US&currency=USD&gad_source=1 | https://www.ebay.com/itm/374993811392?chn=ps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 | https://www.digikey.com/en/products/detail/sparkfun-electronics/11855/5271297?gclsrc=aw.ds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
CR-1025 3V Li+ coin cell | CR-1025-ND | 1 | 1.09 | 1.09 | CR1025 Jauch Quartz | Battery Products | DigiKey (https://www.digikey.com/en/products/detail/jauch-quartz/CR1025/16399048) | https://www.ebay.com/itm/365610739537?chn=ps&google_free_listing_action=view_item
RTC coin cell holder | BK-870 | 1 | 0.58 | 0.58 | BK-870 MPD (Memory Protection Devices) | Battery Products | DigiKey (https://www.digikey.com/en/products/detail/mpd-memory-protection-devices/bk-870/3829737) | https://www.ebay.com/itm/133891769676?chn=ps&google_free_listing_action=view_item
Main PCB | Main board | 1 | 8.23 | 8.23 | https://oshpark.com/
Micro SD card | Gigastone 8GB 10-Pack Micro SD Card, Full HD Video 80MB/s Micro SDHC Class 10 | 1 | 8.24 | 8.24 | https://www.staples.com/centon-micro-8gb-sdhc-memory-card-uhs1-5-pack-s1-msdhu1-8g-5-b/product_24298979?locupd=y | https://www.staples.com/transcend-8gb-microsdhc-memory-card-class-10-ts8gusdhc10/product_IM1LK3226 | https://www.cdwg.com/product/transcend-flash-memory-card-8-gb-microsd/3181432?pfm=srh | https://www.cdwg.com/product/kingston-industrial-flash-memory-card-8-gb-microsdhc-uhs-i/6669743?pfm=srh | https://business.walmart.com/ip/Gigastone-8GB-Micro-SD-Card-FHD-Video-UHS-I-U1-Class-10-Surveillance-Security-Action-Cameras-Drone-Dash-Cams-5-Pack-5x8GB-GS-2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 | https://www.amazon.com/Gigastone-10-Pack-Surveillance-Security-Action/dp/B0876H387X?mcid=a36b7487c2ef3bf38be475383d962644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
Slide switch | 450301014042 | 1 | 2.03 | 2.03 | https://www.digikey.com/en/products/detail/w%C3%BCrth-elektronik/450301014042/5209104 | https://www.mouser.com/ProductDetail/Wurth-Elektronik/450301014042?qs=wr8lucFkNMW0uepaR4R%2Fww%3D%3D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
LED | L314ED | 1 | 0.2 | 0.2 | L314ED American Opto Plus LED | Optoelectronics | DigiKey Marketplace (https://www.digikey.com/en/products/detail/american-opto-plus-led/L314ED/13677700?s=N4IgTCBcDaIDIGYCMAWAogERAXQL5A) | https://www.lvelectronics.com/details/item?itemid=AOP%20L314ED
Resistors | RES SMD (4.7k) OHM 1% 1/4W 1206 | 7 | 0.1 | 0.7 | https://www.digikey.com/en/products/detail/bourns-inc/CR1206-JW-472ELF/3785627 | https://www.mouser.com/ProductDetail/Bourns/CR1206-JW-472ELF?qs=RBg%2F0eAeR6ePTxo24FnKCQ%3D%3D
Resistors | RES SMD (2K) OHM 1% 1/4W 1206 | 7 | 0.1 | 0.7 | https://www.digikey.com/en/products/detail/bourns-inc/CR1206-FX-2001ELF/2562846 | https://www.mouser.com/ProductDetail/KOA-Speer/RK73H2BLTD2001F?qs=iGskpj9dRIVPlylmUlAzCg%3D%3D
Resistors | RES SMD (1k) OHM 1% 1/4W 1206 | 7 | 0.1 | 0.7 | https://www.digikey.com/en/products/detail/bourns-inc/CR1206-FX-1001ELF/2562677 | https://www.mouser.com/ProductDetail/YAGEO/SR1206FR-071KL?qs=k2KEx2DUIRRzYfz4yJHffA%3D%3D
Shunt resistor | ERJ-8BSJR10V RES 0.1 OHM 5\% 1/2W 1206 | 1 | 0.34 | 0.34 | ERJ-8BSJR10V Panasonic Electronic Components | Resistors | DigiKey (https://www.digikey.com/en/products/detail/panasonic-electronic-components/ERJ-8BSJR10V/5647718) | https://www.mouser.com/ProductDetail/Panasonic/ERJ-8BSJR10V?qs=22lEN67Lqx5%2FgSl4VxUkKw%3D%3D
Schottky Diode | SD1206T020S1R0 | 1 | 0.39 | 0.39 | https://www.digikey.com/en/products/detail/kyocera-avx/SD1206T020S1R0/3749511 | https://www.mouser.com/ProductDetail/KYOCERA-AVX/SD1206T020S1R0?qs=jCA%252BPfw4LHaOj8Rzt48dmw%3D%3D
Capacitor 22uF | TAJA226K006RNJ | 1 | 0.41 | 0.41 | https://www.digikey.com/en/products/detail/kyocera-avx/TAJA226K006RNJ/1126793 | https://www.mouser.com/ProductDetail/KYOCERA-AVX/TAJA226K006RNJ?qs=QtLZGLLAmDbrbL0%252BYUNp1A%3D%3D
Capacitor 10uF | ECE-A1EKS100B | 1 | 0.26 | 0.26 | https://www.digikey.com/en/products/detail/panasonic-electronic-components/ECE-A1EKS100B/2689095 | https://www.mouser.com/ProductDetail/Panasonic/ECE-A1EKS100B?qs=rMMd5vBiahpNSBku%2FPA9KQ%3D%3D
Capacitors 0.1uF | C1206S104K5RACAUTO 0.1 uF 10% 50V Ceramic Capacitor X7R 1206 (3216 Metric) | 4 | 0.48 | 1.92 | C1206S104K5RACAUTO KEMET | Capacitors | DigiKey (https://www.digikey.com/en/products/detail/kemet/c1206s104k5racauto/10232834) | https://www.mouser.com/ProductDetail/KEMET/C1206S104K5RACAUTO?qs=ds50AKTGxA9C%252BOGFjvBCPg%3D%3D
5V regulator | MIC5239-5.0YS-TR | 1 | 3.58 | 3.58 | MIC5239-5.0YS-TR Microchip Technology | Integrated Circuits (ICs) | DigiKey (https://www.digikey.com/en/products/detail/microchip-technology/mic5239-5-0ys-tr/2346595) | https://www.microchipdirect.com/product/MIC5239-5.0YS-TR | https://www.mouser.com/ProductDetail/Microchip-Technology/MIC5239-5.0YS-TR?qs=U6T8BxXiZAVR02O8mv9RNQ%3D%3D
PVC pipe | Schedule 40 Clear Pipe, Non-threaded | 4 inch | 2.9 | 2.9 | https://www.grainger.com/product/1AAZ8?gclsrc=aw.ds&gad_source=1&gad_campaignid=21375667808
Female HC-SR04 connector | SSA-104-W-T | 1 | 0.91 | 0.91 | SSA-104-W-T Samtec Inc. | Connectors, Interconnects | DigiKey (https://www.digikey.com/en/products/detail/samtec-inc/ssa-104-w-t/1105908) | https://www.samtec.com/products/ssa-104-w-t
BMS | HX-2S-JH10 | 1 | 2.15 | 2.15 | https://www.ebay.com/itm/122175451692?_skw=2s+7.4v+bms&itmmeta=01JC4ZYQC0WA4Q7FSXJ13Q3MD7 | https://www.ebay.com/itm/386425796959?itmmeta=01JX0567N9MHM61DNDR0TWAKGV
2.54mm JST 3 pin | B3B-XH-A | 1 | 0.13 | 0.13 | https://www.digikey.com/en/products/detail/jst-sales-america-inc/B3B-XH-A/1651046?gad_source=1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 | https://www.ebay.com/itm/135516167050?_skw=B3B-XH-A&itmmeta=01JXJN27KW3SV3ZA95H65390XD
Solar panels | SM141K06TF | 9 | 7.39 | 66.51 | https://www.digikey.com/en/products/detail/anysolar-ltd/SM141K06TF/14311398
M2 nut |  | 2 | 0.01 | 0.02
M2 bolt |  | 2 | 0.073 | 0.14 | https://www.grainger.com/product/Machine-Screws-M2x0-40-Thread-6GY22?
O-Rings |  | 1 | 4.7 | 4.7 | https://www.grainger.com/product/41KX35?RIID=51819294775&GID=729415832&mid=OrderConfirmation_REST&gucid=EMT:11126144:Item:CSM-323&emcid=NA:Item
Total Cost | 194.15

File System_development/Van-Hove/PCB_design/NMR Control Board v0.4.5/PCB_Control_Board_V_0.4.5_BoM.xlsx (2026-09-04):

Internal Part Name | Reference | MFR / Vendor Description | MFR Part Number | Amount per board | Individual Cost | Total Cost | Vendor 1 | Vendor 2 | Vendor 3 | Vendor 4
5 V linear regulator | U3 | IC REG LINEAR 5V 1A DPAK | NCP1117DT50RKG | 1 | $0.52 | $0.52 | https://www.digikey.com/en/products/detail/onsemi/NCP1117DT50RKG/661206?s=N4IgTCBcDaIHIGEAKBGNB2AIgFQKwAYAlAaQHEQBdAXyA | https://www.mouser.com/ProductDetail/onsemi/NCP1117DT50RKG?qs=Gev%252BmEvV0iaGLyZQ1w6kFw%3D%3D | https://www.lcsc.com/product-detail/Low-Dropout-Regulators-LDO_ON-Semicon_NCP1117DT50RKG_ON-Semicon-ON-NCP1117DT50RKG_C152470.html
12 V linear regulator | U5 | IC REG LINEAR 12V 1A D2PAK-3 | MC7812ABD2TR4G | 1 | $0.77 | $0.77 | https://www.digikey.com/en/products/detail/onsemi/MC7812ABD2TR4G/1481258?s=N4IgTCBcDaILIGEDsAOAjGAggIQCJgBUAlAFgHEQBdAXyA | https://www.mouser.com/ProductDetail/onsemi/MC7812ABD2TR4G?qs=%252B9%2Fcbd0IE0Re2wNB1j%2FK%2FQ%3D%3D | https://www.lcsc.com/product-detail/Voltage-Regulators-Linear-Low-Drop-Out-LDO-Regulators_onsemi-MC7812ABD2TR4G_C152478.html?s_z=n_MC7812ABD2TR4G
Inverting charge-pump regulator | U4 | IC REG CHARGE PUMP INV SOT23-5 | LM828M5/NOPB | 1 | $1.25 | $1.25 | https://www.digikey.com/en/products/detail/texas-instruments/LM828M5/2350256 | https://www.mouser.com/ProductDetail/Texas-Instruments/LM828M5-NOPB?qs=QbsRYf82W3GhaXohGcEtsw%3D%3D | https://www.lcsc.com/product-detail/Charge-Pumps_Texas-Instruments-LM828M5-NOPB_C471872.html?s_z=n_LM828M5
Power splitter | Power_Splitter | RF PWR DVDR 1MHZ-650MHZ 6SMD | ADP-2-1W+ | 1 | $11.55 | $11.55 | https://www.digikey.com/en/products/detail/mini-circuits/ADP-2-1W/13680589?s=N4IgTCBcDaIIIBEAKBaMKCMB1A1CAugL5A | https://www.mouser.com/ProductDetail/Mini-Circuits/ADP-2-1W%2b?qs=xZ%2FP%252Ba9zWqaS05pgXAHsTw%3D%3D | https://www.lcsc.com/product-detail/RF-Power-Splitters-Combiners_Mini-Circuits-ADP-2-1W_C879865.html?s_z=n_ADP-2-1W%252B
Mixer | Mixer_Mixer | IC MIXER 50KHZ-250MHZ 6SMD | ADE-6+ | 1 | $10.80 | $10.80 | https://www.digikey.com/en/products/detail/mini-circuits/ADE-6/13927064 | https://www.mouser.com/ProductDetail/Mini-Circuits/ADE-6%2b?qs=xZ%2FP%252Ba9zWqaicAj6d16bRw%3D%3D | https://www.lcsc.com/product-detail/RF-Mixers_Mini-Circuits-ADE-6_C3176578.html?s_z=n_ADE-6%252B
RF switch | U6 | IC RF SWITCH SPST 2.5GHZ 8MSOP | ADG901BRMZ-REEL7 | 1 | $4.03 | $4.03 | https://www.digikey.com/en/products/detail/analog-devices-inc/ADG901BRMZ-REEL7/995401 | https://www.mouser.com/ProductDetail/Analog-Devices/ADG901BRMZ-REEL7?qs=BpaRKvA4VqGtXy7JBFLGiA%3D%3D | https://www.lcsc.com/product-detail/RF-Switches_Analog-Devices-ADG901BRMZ-REEL7_C206802.html?s_z=n_ADG901BRMZ-REEL7
Low-noise operational amplifier | U2 | IC OPAMP GP 1 CIRCUIT 8SSOPB | LM4565FV-GE2 | 1 | $0.61 | $0.61 | https://www.digikey.com/en/products/detail/rohm-semiconductor/LM4565FV-GE2/7896223?s=N4IgTCBcDaIDIFkAsBWAbCgYgNQLQHEBRCAXQF8g | https://www.mouser.com/ProductDetail/ROHM-Semiconductor/LM4565FV-GE2?qs=4v%252BiZTmLVHEiNti1hBVbUQ%3D%3D | https://www.tme.eu/en/details/lm4565fv-ge2/smd-operational-amplifiers/rohm-semiconductor/
1.8 V linear regulator | U1 | IC REG LINEAR 1.8V 50MA SC-88A | NCP715SQ18T2G | 1 | $0.25 | $0.25 | https://www.digikey.com/en/products/detail/onsemi/NCP715SQ18T2G/5257856?s=N4IgTCBcDaIHIGEAKB2AjAVgM4EU0A4AVMAcRAF0BfIA | https://www.mouser.com/ProductDetail/onsemi/NCP715SQ18T2G?qs=dbuNSGnowt1%2Falybo7mueQ%3D%3D | https://www.newark.com/onsemi/ncp715sq18t2g/ic-ldo-volt-reg-0-05a-1-8v-sc/dp/62X8355?CMP=AFC-ECIA
1 µF capacitor | C4, C8, C9 | CAP CER 1UF 5V X7R 1206 | CL31B105KAHNNNE | 3 | $0.13 | $0.39 | https://www.digikey.com/en/products/detail/samsung-electro-mechanics/CL31B105KAHNNNE/3886755?s=N4IgTCBcDaIMIBkDMBGAQigDAVgNIEEAJAOVIFEQBdAXyA | https://www.mouser.com/ProductDetail/Samsung-Electro-Mechanics/CL31B105KAHNNNE?qs=349EhDEZ59p5FHnPIxx1UQ%3D%3D | https://www.lcsc.com/product-detail/Multilayer-Ceramic-Capacitors-MLCC-SMD-SMT_Samsung-Electro-Mechanics-CL31B105KAHNNNE_C28322.html?s_z=n_CL31B105KAHNNNE
0.1 µF capacitor | C10, C11, C12 | CAP CER 0.1UF 50V X7R 1206 | CL31B104KBCNNNC | 3 | $0.11 | $0.33 | https://www.digikey.com/en/products/detail/samsung-electro-mechanics/CL31B104KBCNNNC/3886675?s=N4IgTCBcDaIMIBkDMBGAQigDAFgNJrgDli4QBdAXyA | https://www.mouser.com/ProductDetail/Samsung-Electro-Mechanics/CL31B104KBCNNNC?qs=349EhDEZ59oHABbyGq1iKA%3D%3D | https://www.lcsc.com/product-detail/Multilayer-Ceramic-Capacitors-MLCC-SMD-SMT_Samsung-Electro-Mechanics-CL31B104KBCNNNC_C24497.html?s_z=n_CL31B104KBCNNNC
1 nF capacitor | C13, C14 | CAP CER 1000PF 2KV X7R 1206 | VPDD202W102K1GV001E | 2 | $0.19 | $0.38 | https://www.digikey.com/en/products/detail/johanson-dielectrics-inc/VPDD202W102K1GV001E/1556359?s=N4IgTCBcDaIGoAUAiSwAYwHUCMGDS2A4nGmtgKIgC6AvkA | https://www.mouser.com/ProductDetail/Johanson-Dielectrics/VPDD202W102K1GV001E?qs=jRuttqqUwMTOgYz3gUWN7g%3D%3D | https://www.newark.com/johanson-dielectrics/202r18w102kv4e/ceramic-capacitor-1000pf-2000v/dp/01H9029
0.33 µF capacitor | C5 | CAP CER 0.33UF 50V X7R 1206 | CL31B334KBFNNNE | 1 | $0.18 | $0.18 | https://www.digikey.com/en/products/detail/samsung-electro-mechanics/CL31B334KBFNNNE/3886796?s=N4IgTCBcDaIMIBkDMBGAQkpAWA0mgYgHLECiIAugL5A | https://www.mouser.com/ProductDetail/Samsung-Electro-Mechanics/CL31B334KBFNNNE?qs=349EhDEZ59qKxGVb2dY2bQ%3D%3D | https://www.lcsc.com/product-detail/Multilayer-Ceramic-Capacitors-MLCC-SMD-SMT_Samsung-Electro-Mechanics-CL31B334KBFNNNE_C307572.html?s_z=n_CL31B334KBFNNNE
10 µF capacitor | C1, C2, C3, C15 | CAP CER 10UF 6.3V X5R 1206 | CL31A106KQHNNNE | 4 | $0.19 | $0.76 | https://www.digikey.com/en/products/detail/samsung-electro-mechanics/CL31A106KQHNNNE/3886737?s=N4IgTCBcDaIMIBkDMBGAgigDANgNIEUAJAOVIFEQBdAXyA | https://www.mouser.com/ProductDetail/Samsung-Electro-Mechanics/CL31A106KQHNNNE?qs=349EhDEZ59pJO7ndoI%2FMkg%3D%3D | https://www.newark.com/samsung-electro-mechanics/cl31a106kbhnnne/cap-10uf-50v-mlcc-1206/dp/82AC9486
62 pF capacitor | C7 | CAP CER 62PF 50V C0G/NP0 0603 | 06035A620JAT2A | 1 | $0.10 | $0.10 | https://www.digikey.com/en/products/detail/kyocera-avx/06035A620JAT2A/1599919 | https://www.mouser.com/ProductDetail/KYOCERA-AVX/06035A620JAT2A?qs=VYVmvnYLdvmMNkKlwnY2DA%3D%3D | https://www.newark.com/kyocera-avx/06035a620jat2a/capacitor-62pf-c0g-np0-50v-0603/dp/41AM3452
68 pF capacitor | C6 | CAP CER 68PF 50V C0G/NP0 0402 | CL05C680JB51PNC | 1 | $0.10 | $0.10 | https://www.digikey.com/en/products/detail/samsung-electro-mechanics/CL05C680JB51PNC/5961075 | https://www.mouser.com/ProductDetail/Samsung-Electro-Mechanics/CL05C680JB51PNC?qs=Qj6zq1TuXccLoUfUcVMRpg%3D%3D | https://www.tme.com/in/en/details/cl05c680jb51pnc/mlcc-smd-capacitors/samsung/
General-purpose diode | D1, D2, D3, D4 | DIODE GEN PURP 100V 200MA DO35 | 1N4148-T50R | 4 | $0.10 | $0.40 | https://www.digikey.com/en/products/detail/onsemi/1N4148-T50R/978510?s=N4IgTCBcDaIIwDkAsckA4C0AVArABgCUQBdAXyA | https://www.mouser.com/ProductDetail/onsemi-Fairchild/1N4148-T50R?qs=0lQeLiL1qyZS6rosZp7Ehg%3D%3D | https://www.newark.com/onsemi/1n4148-t50r/small-signal-sw-diode-100v-0-2a/dp/48AC1509
Schottky diode array | D8, D9, D10 | DIODE ARRAY SCHOTTKY 40V SOT23 | BAT6404E6433HTMA1 | 3 | $0.46 | $1.38 | https://www.digikey.com/en/products/detail/infineon-technologies/BAT6404E6433HTMA1/1280948?s=N4IgTCBcDaIEIEEAqA2ALABjQUXQZjwAkkBZBARhAF0BfIA | https://www.mouser.com/ProductDetail/Infineon-Technologies/BAT6404E6433HTMA1?qs=K00xGehIlju31KA4KMtgCQ%3D%3D | https://www.newark.com/infineon/bat6404e6433htma1/diode-schottky-aec-q101-40v-sot23/dp/68AC4382
Female through-hole SMA connector | J1-J12 | CONN SMA JACK STR 50OHM PCB | RF2-04A-T-00-50-G | 12 | $1.84 | $22.08 | https://www.digikey.com/en/products/detail/adam-tech/RF2-04A-T-00-50-G/9830588 | https://www.mouser.com/ProductDetail/Adam-Tech/RF2-04A-T-00-50-G?qs=HoCaDK9Nz5dc3qwWN4DjGA%3D%3D | https://www.heilind.com/adtrf2-04a-t-00-50-g.html?&utm_source=octopart&utm_medium=buy | https://www.aliexpress.us/item/3256804056009500.html?curPageLogUid=FLqHVcrTDnmC
 |  |  |  |  | Total Cost | $55.88

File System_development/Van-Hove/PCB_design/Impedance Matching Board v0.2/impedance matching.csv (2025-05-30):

Id | Designator | Footprint | Quantity | Designation | Supplier and ref
1 | CM | C_Rect_L7.0mm_W6.0mm_P5.00mm | 1 | C_Variable
2 | CT | C_Trim_GZD10100 | 1 | C_Trim_3_Leg
3 | J1,J2 | SMA_Amphenol_132203-12_Horizontal | 2 | Conn_Coaxial

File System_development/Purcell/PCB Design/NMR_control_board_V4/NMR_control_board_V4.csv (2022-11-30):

Source: | C:\Users\localuser\OneDrive - University of South Carolina\NMR Research\KiCad (PCBs)\v0.2\NMR_control_board_V4\NMR_control_board_V4.kicad_sch
Date: | 8/18/2022 14:06
Tool: | Eeschema (6.0.1)
Generator: | C:\Program Files\KiCad\6.0\bin\scripting\plugins/bom_csv_grouped_by_value.py
Component Count: | 23
Individual Components:
Item | Qty | Reference(s) | Value | LibPart | Footprint | Datasheet
 |  | 5V1 | Conn_Coaxial | Connector:Conn_Coaxial | Connector_Coaxial:SMA_Samtec_SMA-J-P-X-ST-EM1_EdgeMount | ~
 |  | -5V1 | Conn_Coaxial | Connector:Conn_Coaxial | Connector_Coaxial:SMA_Samtec_SMA-J-P-X-ST-EM1_EdgeMount | ~
 |  | C1 | C | Device:C | Capacitor_SMD:C_1206_3216Metric | ~
 |  | C2 | 1 uF | pspice:C | Capacitor_SMD:C_1206_3216Metric | ~
 |  | C3 | C | Device:C | Capacitor_SMD:C_1206_3216Metric | ~
 |  | C4 | 1 uF | pspice:C | Capacitor_SMD:C_1206_3216Metric | ~
 |  | C5 | 0.1 uF | pspice:C | Capacitor_SMD:C_1206_3216Metric | ~
 |  | C6 | 0.1uF | Device:C | Capacitor_SMD:C_1206_3216Metric | ~
 |  | C7 | 0.1uF | Device:C | Capacitor_SMD:C_1206_3216Metric | ~
 |  | F_OUT1 | Conn_Coaxial | Connector:Conn_Coaxial | Connector_Coaxial:SMA_Samtec_SMA-J-P-X-ST-EM1_EdgeMount | ~
 |  | MIX_RF1 | Conn_Coaxial | Connector:Conn_Coaxial | Connector_Coaxial:SMA_Samtec_SMA-J-P-X-ST-EM1_EdgeMount | ~
 |  | R1 | R | Device:R | Resistor_SMD:R_1206_3216Metric | ~
 |  | R2 | R | Device:R | Resistor_SMD:R_1206_3216Metric | ~
 |  | R3 | R | Device:R | Resistor_SMD:R_1206_3216Metric | ~
 |  | R4 | R | Device:R | Resistor_SMD:R_1206_3216Metric | ~
 |  | SPL_IN1 | Conn_Coaxial | Connector:Conn_Coaxial | Connector_Coaxial:SMA_Samtec_SMA-J-P-X-ST-EM1_EdgeMount | ~
 |  | SW_CTRL1 | Conn_Coaxial | Connector:Conn_Coaxial | Connector_Coaxial:SMA_Samtec_SMA-J-P-X-ST-EM1_EdgeMount | ~
 |  | SW_OUT1 | Conn_Coaxial | Connector:Conn_Coaxial | Connector_Coaxial:SMA_Samtec_SMA-J-P-X-ST-EM1_EdgeMount | ~
 |  | U1 | LM4565 | LM4565 Operational Amplifier:LM4565 | Package_SO:TSSOP-8_4.4x3mm_P0.65mm
 |  | U2 | NCP715-1.8V | NCP715:NCP715-1.8V | Package_TO_SOT_SMD:SOT-353_SC-70-5
 |  | U3 | ADP-2-1W | RF:ADP-2-1W | RF_Mini-Circuits:Mini-Circuits_CD636_LandPatternPL-035 | https://www.minicircuits.com/pdfs/ADP-2-1W.pdf
 |  | U4 | ADG901BRMZ | RF_Switch:ADG901BRMZ | Package_SO:MSOP-8_3x3mm_P0.65mm | https://www.analog.com/media/en/technical-documentation/data-sheets/ADG901_902.pdf
 |  | U5 | ADE-6 | RF_Mixer:ADE-6 | RF_Mini-Circuits:Mini-Circuits_CD542_LandPatternPL-052 | https://www.minicircuits.com/pdfs/ADE-6.pdf
Collated Components:
Item | Qty | Reference(s) | Value | LibPart | Footprint | Datasheet
1 | 7 | 5V1, -5V1, F_OUT1, MIX_RF1, SPL_IN1, SW_CTRL1, SW_OUT1 | Conn_Coaxial | Connector:Conn_Coaxial | Connector_Coaxial:SMA_Samtec_SMA-J-P-X-ST-EM1_EdgeMount | ~
2 | 2 | C1, C3 | C | Device:C | Capacitor_SMD:C_1206_3216Metric | ~
3 | 2 | C2, C4 | 1 uF | pspice:C | Capacitor_SMD:C_1206_3216Metric | ~
4 | 1 | C5 | 0.1 uF | pspice:C | Capacitor_SMD:C_1206_3216Metric | ~
5 | 2 | C6, C7 | 0.1uF | Device:C | Capacitor_SMD:C_1206_3216Metric | ~
6 | 4 | R1, R2, R3, R4 | R | Device:R | Resistor_SMD:R_1206_3216Metric | ~
7 | 1 | U1 | LM4565 | LM4565 Operational Amplifier:LM4565 | Package_SO:TSSOP-8_4.4x3mm_P0.65mm
8 | 1 | U2 | NCP715-1.8V | NCP715:NCP715-1.8V | Package_TO_SOT_SMD:SOT-353_SC-70-5
9 | 1 | U3 | ADP-2-1W | RF:ADP-2-1W | RF_Mini-Circuits:Mini-Circuits_CD636_LandPatternPL-035 | https://www.minicircuits.com/pdfs/ADP-2-1W.pdf
10 | 1 | U4 | ADG901BRMZ | RF_Switch:ADG901BRMZ | Package_SO:MSOP-8_3x3mm_P0.65mm | https://www.analog.com/media/en/technical-documentation/data-sheets/ADG901_902.pdf
11 | 1 | U5 | ADE-6 | RF_Mixer:ADE-6 | RF_Mini-Circuits:Mini-Circuits_CD542_LandPatternPL-052 | https://www.minicircuits.com/pdfs/ADE-6.pdf

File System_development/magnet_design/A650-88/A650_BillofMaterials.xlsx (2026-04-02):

BILL OF MATERIALS
Designator | Component | Amount | Individual Cost | Total Cost | Vendor 1 | Vendor 2 | Vendor 3 | Vendor 4
Iron Yoke | Carbon Steel Rectangular Bar: 1018, 0.75 in Thick, 3 1/2 in x 36 in Nominal Size (WxL), -0.003 in | 1 | $105.00 | $105.00 | https://www.grainger.com/product/Carbon-Steel-Rectangular-Bar-2HHV2?opr=PLADS&analytics=FM%3APLA&a2c_sku_original=2HHT9&position=3
N42 Disc Magnet | 3 x 1 Inch Neodymium Rare Earth Disc Magnet N42 DZ0X0 | 2 | $207.71 | $415.42 | https://www.kjmagnetics.com/dz0x0-neodymium-disc-magnet
Enamel Transparent Paint | Rust Preventative Spray Paint: Std Spray Paints, Rust Preventative, Clear, Metal/Wood | 1 | $17.91 | $17.91 | RUST-OLEUM, Std Spray Paints, Rust Preventative, Rust Preventative Spray Paint - 42PR84|7701830 - Grainger (https://www.grainger.com/product/42PR84?RIID=51819294775&GID=729415832&mid=OrderConfirmation_REST&gucid=EMT:11126144:Item:CSM-323&emcid=NA:Item)
Painter Tape | Tape: 3/4 in Wd, 60 yd Lg, 5.1 mil Thick, Blue, 2 wk Clean Removal Time | 2 | $5.49 | $10.98 | https://www.grainger.com/product/497C31?RIID=51819294775&GID=729415832&mid=OrderConfirmation_REST&gucid=EMT:11126144:Item:CSM-323&emcid=NA:Item
Dielectric Grease | SUPER LUBE Heat Conducting Compound | 1 | $14.50 | $14.50 | https://www.grainger.com/product/44N787?RIID=51819294775&GID=729415832&mid=OrderConfirmation_REST&gucid=EMT:11126144:Item:CSM-323&emcid=NA:Item
HDPE Sheet | 0.5 in Thick, 12 in x 24 in, Opaque, Off-White | 1 | $29.76 | $29.76 | https://www.grainger.com/product/HDPE-Sheet-0-5-in-Thick-22JM75?opr=ODOH&analytics=FM:Order%20History
HDPE Sheet | 0.125 in Thick, 12 in x 24 in, Opaque, Off-White | 1 | $19.99 | $19.99 | https://www.grainger.com/product/1ZAH9?RIID=51819294775&GID=729415832&mid=OrderConfirmation_REST&gucid=EMT:11126144:Item:CSM-323&emcid=NA:Item
DIN Rail | Aluminum, 35 mm Wd, 1 m Lg | 1 | $11.21 | $11.21 | https://www.grainger.com/product/18Z758?RIID=51819294775&GID=729415832&mid=OrderConfirmation_REST&gucid=EMT:11126144:Item:CSM-323&emcid=NA:Item
HDPE Sheet | 0.75 in Thick, 12 in x 24 in, Opaque | 1 | $46.30 | $46.30 | https://www.grainger.com/product/1ZAJ5?RIID=51819294775&GID=729415832&mid=OrderConfirmation_REST&gucid=EMT:11126144:Item:CSM-323&emcid=NA:Item

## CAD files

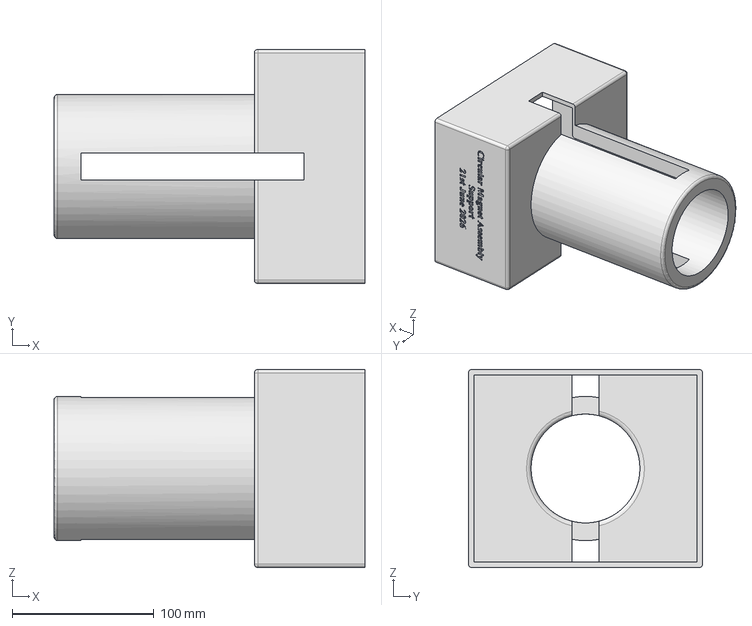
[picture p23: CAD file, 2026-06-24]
System_development/magnet_design/A650-290/CAD/assembly_tools/Magnet_Assembly_Support.stp
219.2 x 165.1 x 139.7 mm

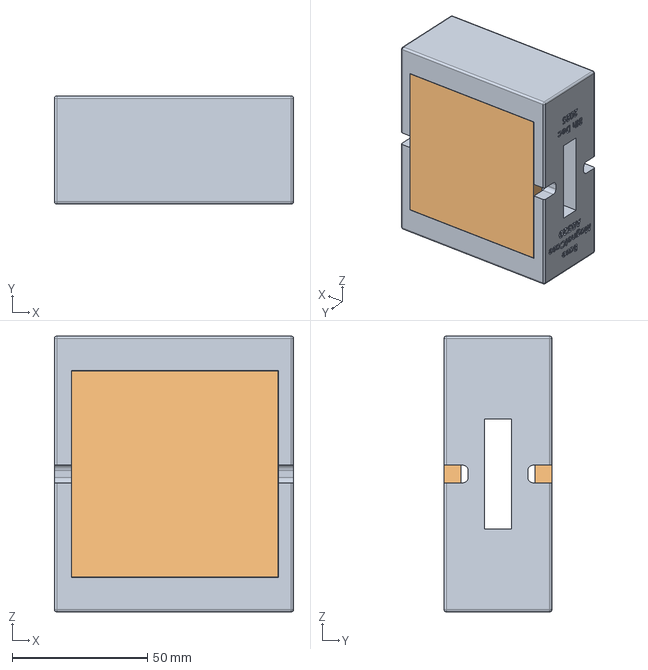
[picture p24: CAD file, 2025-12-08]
System_development/magnet_design/A320-53/CAD/assembly_tools/A320_Case_Assembly.stp
88.5 x 40.0 x 102.0 mm
Base_Casing_A0645_v2
Sample_magnet_3_3_0.25 x 2

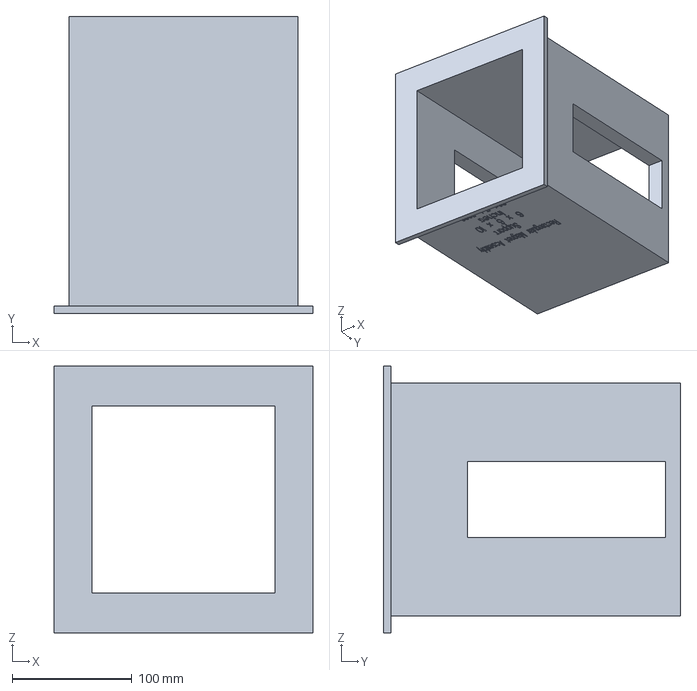
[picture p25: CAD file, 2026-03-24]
System_development/magnet_design/A650-290/CAD/assembly_tools/Assembly_6x6x10.stp
215.9 x 247.6 x 222.2 mm

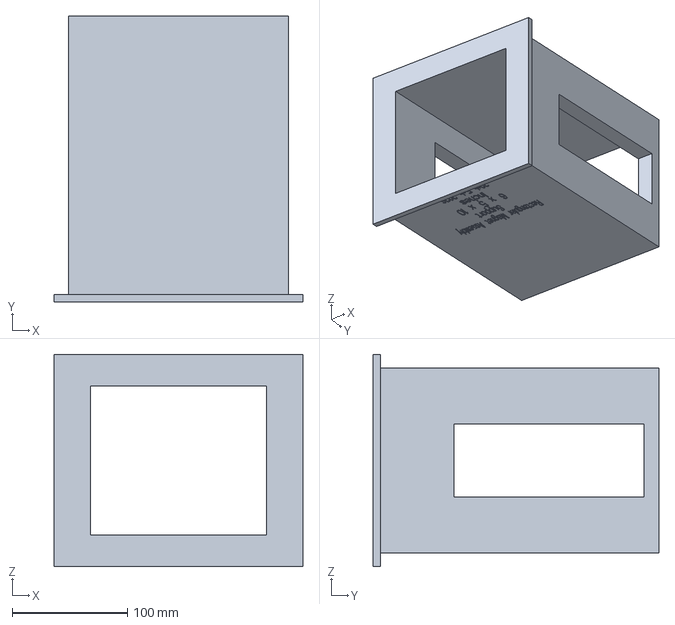
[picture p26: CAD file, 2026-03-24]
System_development/magnet_design/A650-290/CAD/assembly_tools/Assembly_6x5x10.stp
215.9 x 247.6 x 184.1 mm

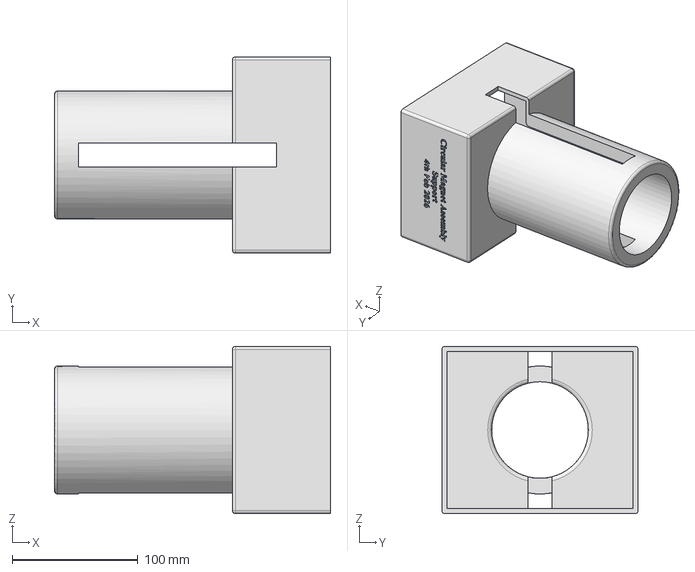
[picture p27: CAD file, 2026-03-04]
System_development/magnet_design/A650-290/CAD/assembly_tools/Assembly_Support.stp
219.2 x 156.0 x 133.0 mm

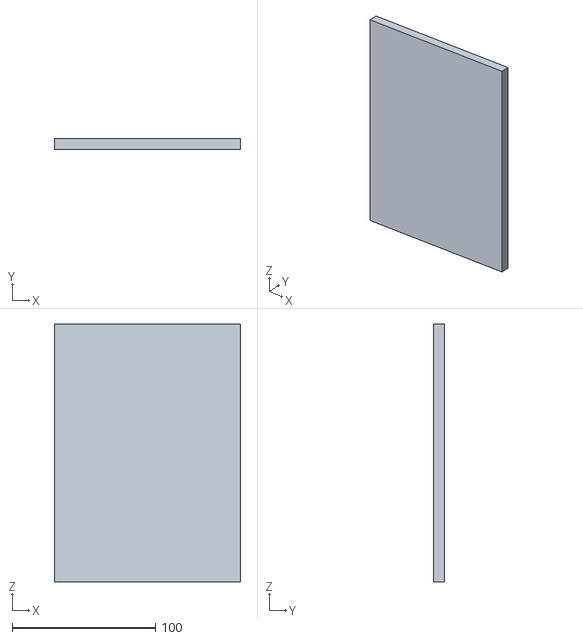
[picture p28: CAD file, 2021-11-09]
System_development/Bloch/3D Print Files/5mm_tube_sample_holder/v1/Side Support NMR.stl
130.0 x 7.50 x 180.0

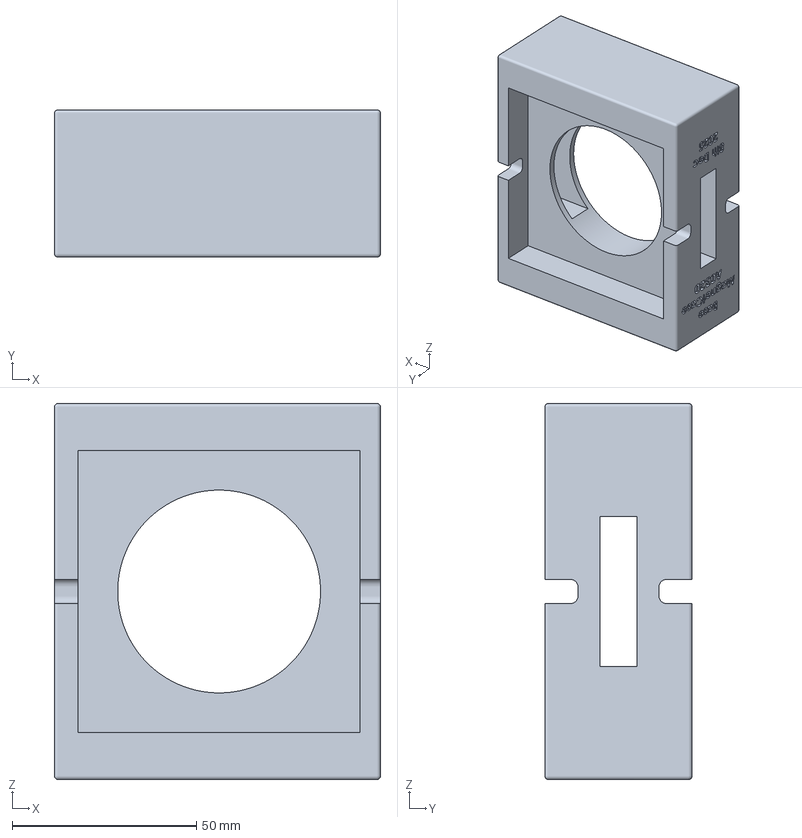
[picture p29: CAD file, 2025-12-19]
System_development/magnet_design/A320-53/CAD/assembly_tools/A320_Case_Assamble.3mf
88.5 x 40.0 x 102.0 mm

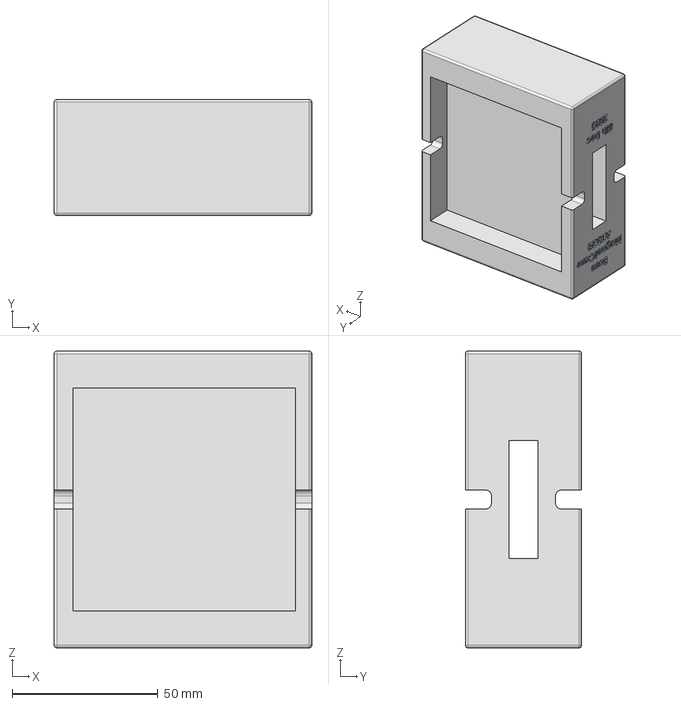
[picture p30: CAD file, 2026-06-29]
System_development/magnet_design/A320-53/CAD/Base_Casing_A0320.stp
88.5 x 40.0 x 102.0 mm

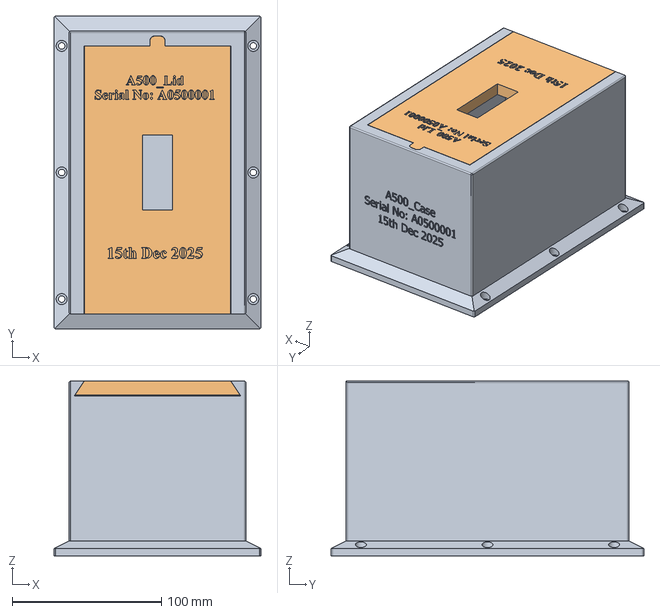
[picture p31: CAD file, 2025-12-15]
System_development/magnet_design/A500-74/CAD/Boxcover_and_Lid_A500.stp
138.2 x 209.4 x 117.0 mm

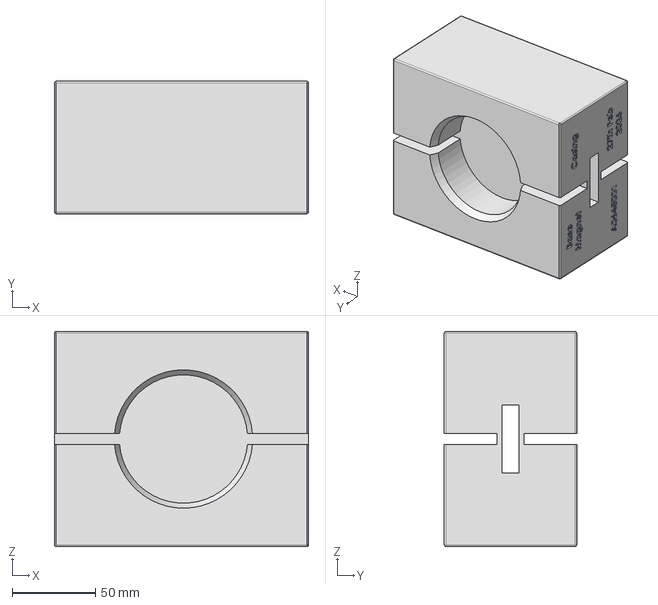
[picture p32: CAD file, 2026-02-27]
System_development/magnet_design/A650-290/CAD/Base_Casing_A0645.stp
152.4 x 79.5 x 129.1 mm

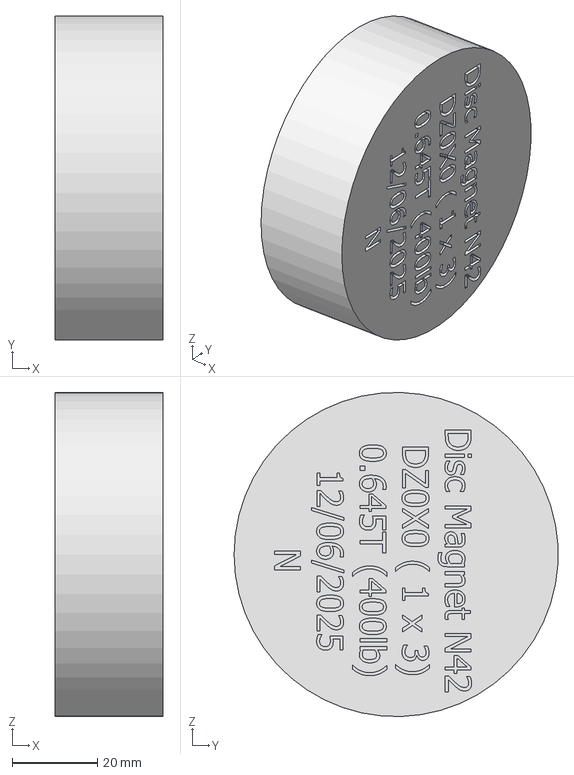
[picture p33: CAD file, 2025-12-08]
System_development/magnet_design/A650-88/CAD/assembly_tools/Sample_Magnet.stp
25.4 x 76.1 x 76.2 mm

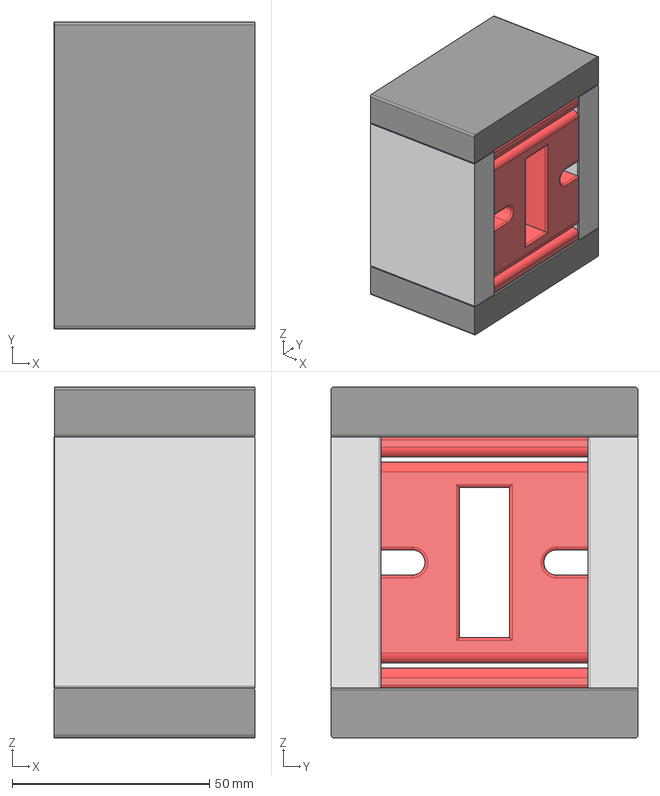
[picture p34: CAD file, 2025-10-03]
System_development/magnet_design/A650-88/CAD/b645magnet_CAD.stp
50.9 x 77.8 x 88.9 mm
b645left
b645left_1
b645front
b645front_1
b645resin

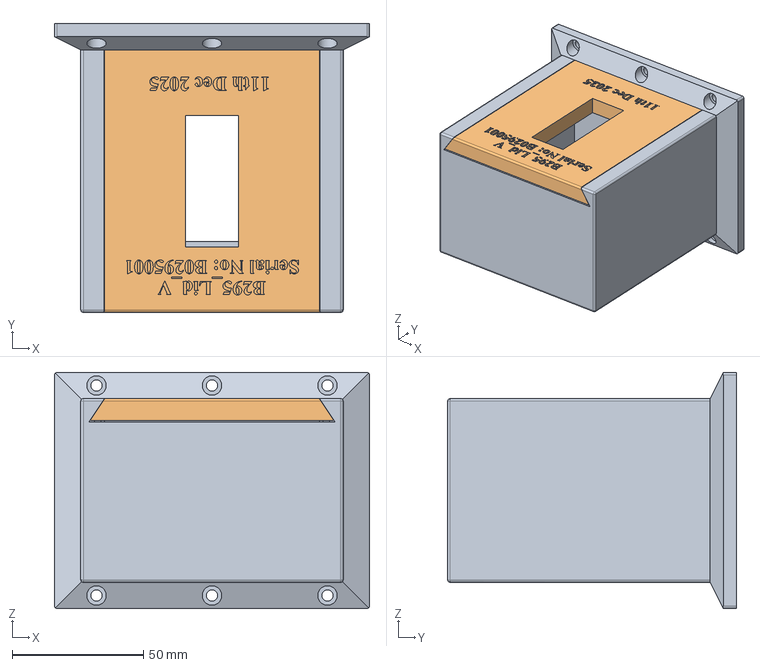
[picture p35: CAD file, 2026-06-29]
System_development/magnet_design/B300-20/CAD/Boxcover_and_Lid_flow_through_B295.stp
120.0 x 110.0 x 90.0 mm

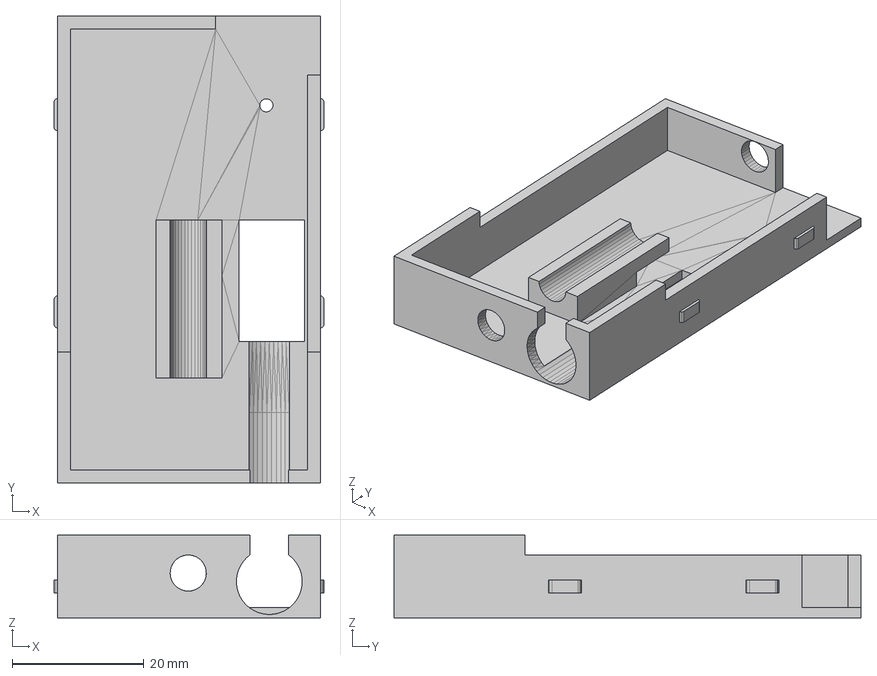
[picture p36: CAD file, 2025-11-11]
System_development/magnet_design/B570-20/CAD/tray.stp
41.0 x 71.0 x 12.6 mm

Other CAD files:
System_development/Bloch/3D Print Files/TRAY 3x1 v11.stp
System_development/Gill/3D prints/Small Magnet tray v0.4.2.step
System_development/magnet_design/0.645_Tesla_magnet/CAD/magnet tray.step
System_development/magnet_design/B570_Tesla_magnet/CAD/Boxcover_and_Lid_570_detent6_vertical.stp
System_development/Bloch/3D Print Files/5mm_tube_sample_holder/v1/Hole Ends NMR.stl
System_development/Bloch/3D Print Files/5mm_tube_sample_holder/v1/Holes NMR.stl
System_development/Bloch/3D Print Files/TWO MAG BODY 1.5x1.5 v3.stp
System_development/Bloch/3D Print Files/TWO MAG BODY 3x1 v13.stp
System_development/Gill/3D prints/Small Magnet tray v0.4.2.f3d
System_development/Purcell/3D Print Files/Magnet/Mag Body 3x1.5 V02 v1.stp
System_development/Purcell/3D Print Files/Magnet/MagBody 3x1.5 V02 v1.stp
System_development/Purcell/3D Print Files/Magnet/TWO MAG BODY 3x1.5 v01.stp
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

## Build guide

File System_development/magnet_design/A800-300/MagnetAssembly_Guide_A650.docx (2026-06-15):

NMR Magnet Assembly

# 1. Overview

This is a step-by-step guide for building a new NMR magnet using the assembly fixtures made for it. The parts are the magnet core, the permanent magnets, thin steel center plates, thick steel side plates, and a set of HDPE strips.

The magnets are strong and will snap together hard if you let them. The point of the fixtures is to lower each magnet slowly and keep everything lined up. Work carefully and keep your hands out of the gap.

# 2. Safety

Magnets are the main hazard. They can crush a finger, chip or crack on impact, and pull in nearby steel. Keep them under control the whole time.

- Seat magnets with the insertion tool and strips, not with your hands between two magnetic faces.
- Never let a magnet drop in free. Lower it gradually using the strips.
- Keep loose steel tools, screws, and other magnets away from the work area.
- Wear safety glasses. Magnets can fracture and throw pieces if they hit each other.
- Keep phones, drives, cards, and watches away. Anyone with a pacemaker or implant should stay clear.
- Have a second person or third person help hold the fixture and hand off parts during the assembly.

# 3. Parts and Tools

Have everything ready before you start.

Part | Description
Magnet core | The block with the magnet size hole. Each magnet sits in this pocket.
Magnet Assembly Tool | The fixture with the round boss. It pushes each magnet straight down into the pocket.
Side frames (2 sizes) | The open frames with side windows. They hold the stack so you can slide the thick side plates in. Two sizes, one for each plate size.
HDPE strips | Thin strips cut from HDPE sheet. You stack them under a magnet and pull them out one at a time to bring them down slowly.
Magnets | The NMR magnets
Center plates | Thin steel discs cut to the magnet size and ground flat. They go against magnet faces to make the field more even.
Side plates | Thick steel plates that go on the four sides at the end to keep the field inside. Two sizes.

# 4. Prepare the Center Plates

Do this before handling any magnets.

1. Cut the thin steel plates to the magnet size.
2. Grind or lap each plate flat and smooth so the magnet seats fully against it.
3. Deburr the edges, wipe the plates clean, and set them aside away from the magnets.

A burr or bit of dirt under a plate leaves a small gap that throws off the field, so it is worth getting these flat.

# 5. Build the Magnet Stack

Work on a flat clean surface with the core pocket facing up. Keep the insertion tool and strips within reach and wear safety glasses.

1. Place a center plate flat in the bottom of the pocket. Check it sits flush with no rocking.
2. Lay HDPE strips across the pocket to make a platform that holds the magnet above the plate.
3. Load the magnet onto the magnet assembly tool so it stays square. Keep your hands on the tool, not in the gap.
4. Lower the magnet with the tool until it rests on the strips, not yet on the plate.
5. Pull the strips out one at a time. The magnet steps down a little with each one until it sits on the plate.
6. Check the magnet is seated flat and centered.
7. Place the next center plate on the other side of the core and lower it by using the same magnet assembly tool.
8. Lower the second magnet the same way. Check its orientation before bringing it down.
9. Repeat for any more magnet and plate layers the design needs.

# 6. Add the Side Plates

With the magnets and plates stacked, add the thick steel plates on the four sides using the frames.

1. Pick the frame that matches the plate size (there are two).
2. Set the stack in the frame so a side window line up with the side you are filling.
3. If needed, use strips to hold the plate slightly out so it goes in under control instead of slamming.
4. Pull the strips and slide the plate against the stack until it sits flat.
5. Do all four sides, switching frame size when the plate size changes.
6. Check each plate is seated against the stack with no gaps. Use the dead blow hammer to adjust the plates.

# 7. Final Check

- Confirm every layer is flat and centered and all four side plates are flush. Use dead blow hammer if needed.
- Look for any pinched strip, debris, or gap between faces.
- Measure the field with a gaussmeter and compare it to what you expect for this magnet.

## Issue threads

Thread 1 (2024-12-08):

### ISSUE TITLE
Reg dimension of the bar magnets for B645 arrangement

### ISSUE THREAD

**Issue by abanerjee123** [ARTS-Laboratory/Compact-NMR#1]
<img width="372" alt="Polarization_Plot" src="https://github.com/user-attachments/assets/cb0ff086-5020-4a8a-9008-f54d9a2eab2d">
Hi
       I am interested to make a small magnet for a desktop NMR system. I am interested in the 10 magnet arrangement. Could you share the dimension of the 10 magnets used in the B645 arrangement? 

Thanks 
Abhishek

file:///home/abhishek/FPGA_devel/Compact-NMR-master/System_development/magnet_design/B645_Tesla_magnet/media/Polarization_Plot.PNG

**Comment by austindowney** [comment]
Of course, the magnet part numbers are "BX8X88" and "BX844" from KJ Magnets.

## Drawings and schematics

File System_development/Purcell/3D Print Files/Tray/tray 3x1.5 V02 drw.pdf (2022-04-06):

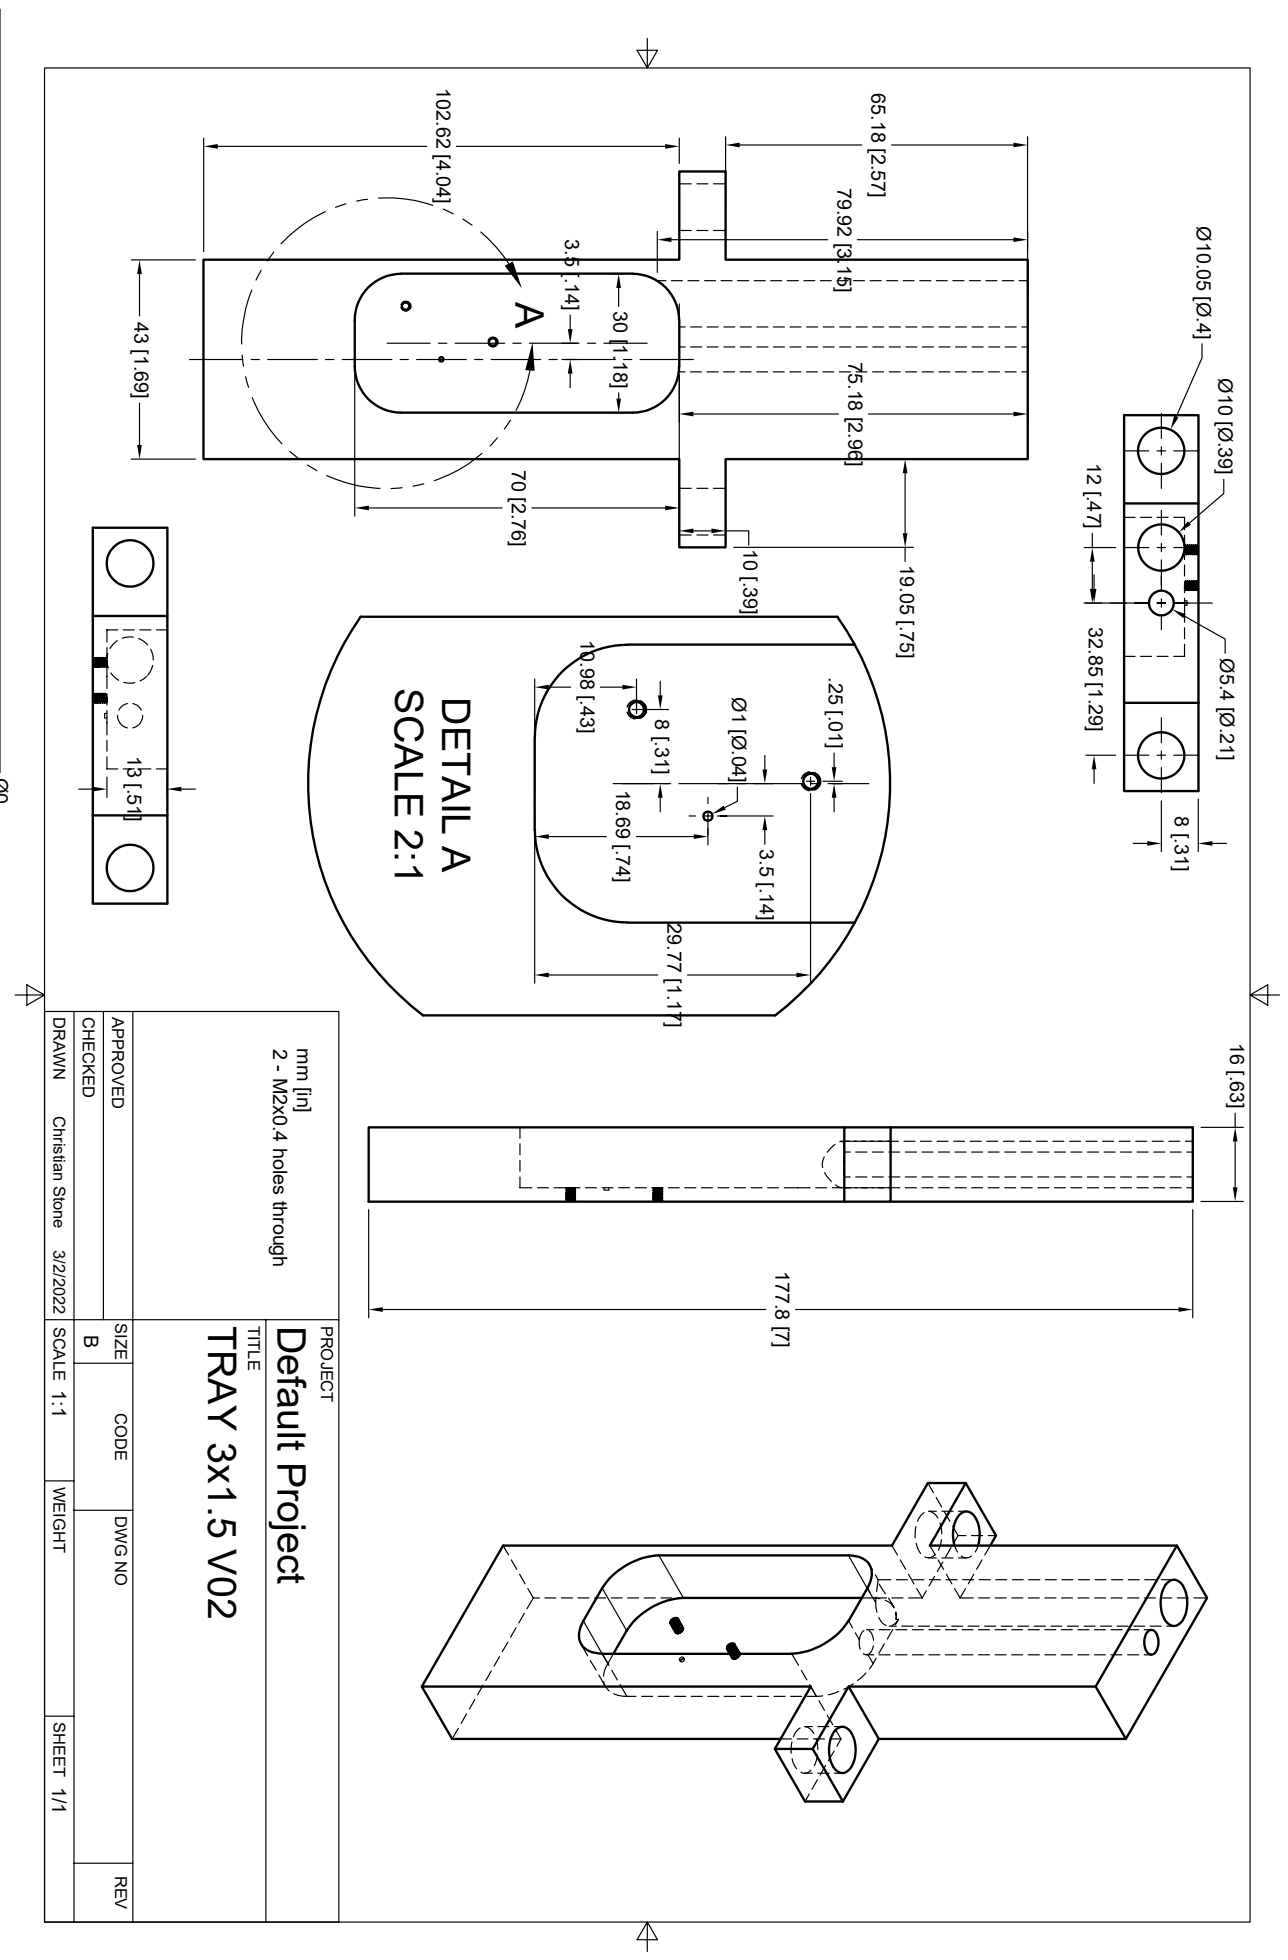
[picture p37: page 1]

TITLE PROJECT DRAWN CHECKED APPROVED SCALE WEIGHT SHEET DWG NO REV CODE SIZE 1/1 1:1 3/2/2022 Christian Stone BTRAY 3x1.5 V02 Default Project 43 [1.69] A SCALE 2:1 DETAIL A .25 [.01] 8 [.31] 10.98 [.43] 29.77 [1.17] 3.5 [.14] 18.69 [.74] Ø1 [Ø.04] 3.5 [.14] 10 [.39] 65.18 [2.57] 75.18 [2.96] 79.92 [3.15] 70 [2.76] 30 [1.18] 102.62 [4.04] 19.05 [.75] Ø10.05 [Ø.4] Ø5.4 [Ø.21] Ø10 [Ø.39]12 [.47] 32.85 [1.29] 8 [.31] 13 [.51] 177.8 [7] mm [in] 16 [.63] 2 - M2x0.4 holes through

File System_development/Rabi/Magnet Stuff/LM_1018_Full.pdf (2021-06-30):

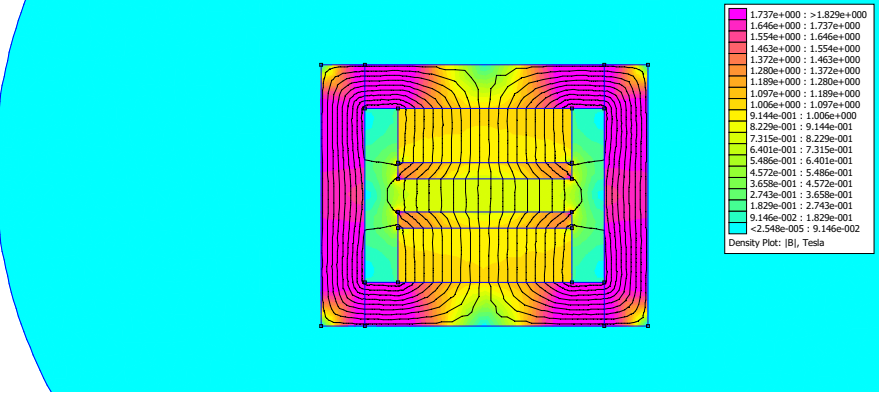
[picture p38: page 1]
Density Plot: |B|, Tesla

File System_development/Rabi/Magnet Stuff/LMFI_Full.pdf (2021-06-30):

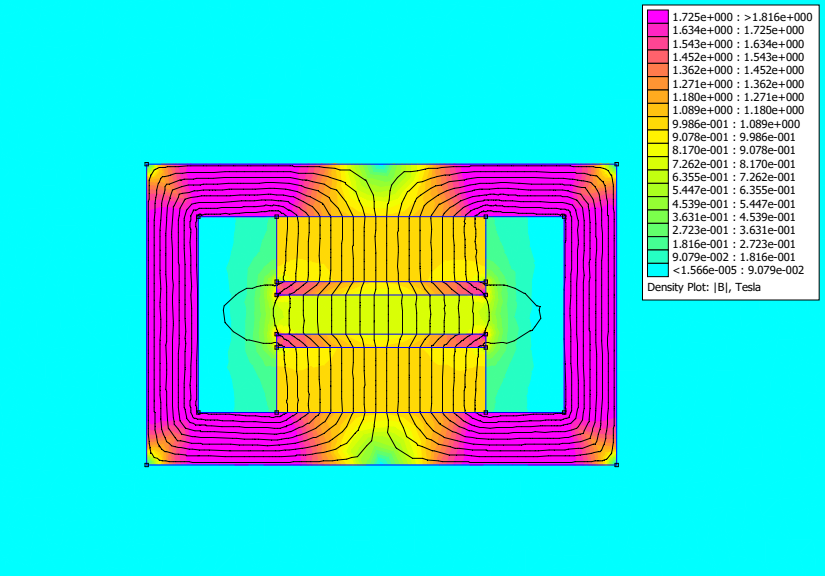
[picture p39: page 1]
Density Plot: |B|, Tesla

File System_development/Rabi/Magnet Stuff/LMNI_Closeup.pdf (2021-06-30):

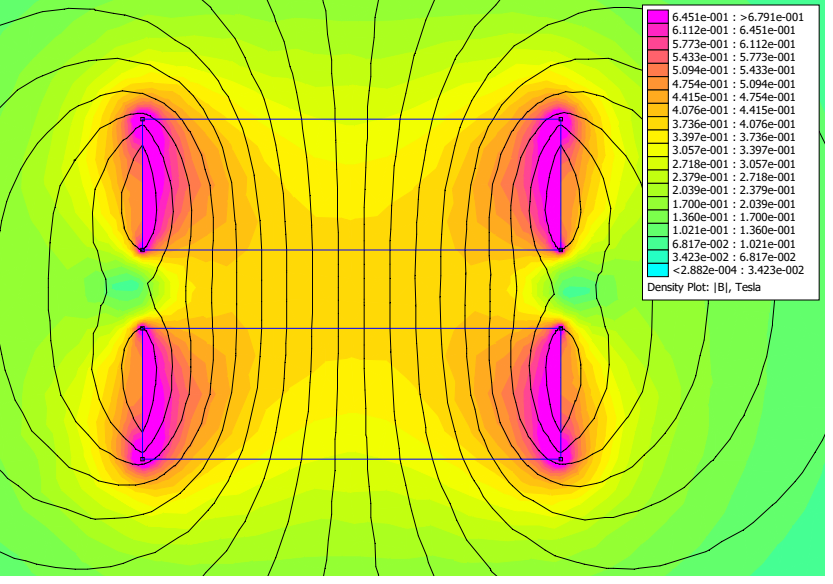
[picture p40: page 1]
Density Plot: |B|, Tesla

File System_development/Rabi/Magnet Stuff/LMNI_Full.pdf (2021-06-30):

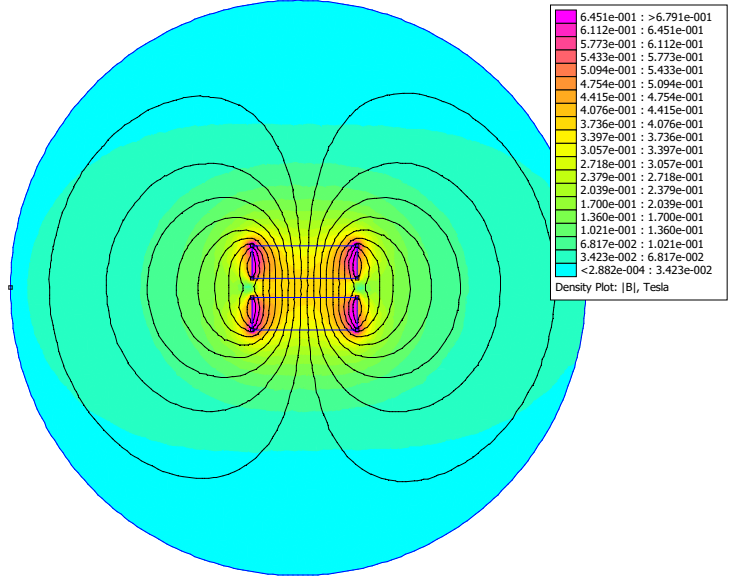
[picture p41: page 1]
Density Plot: |B|, Tesla

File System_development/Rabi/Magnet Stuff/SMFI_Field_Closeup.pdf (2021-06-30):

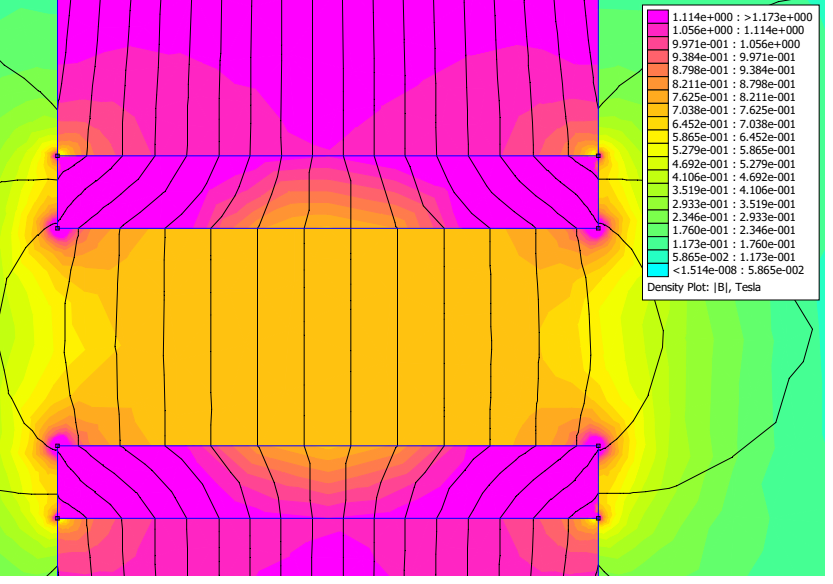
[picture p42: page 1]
Density Plot: |B|, Tesla

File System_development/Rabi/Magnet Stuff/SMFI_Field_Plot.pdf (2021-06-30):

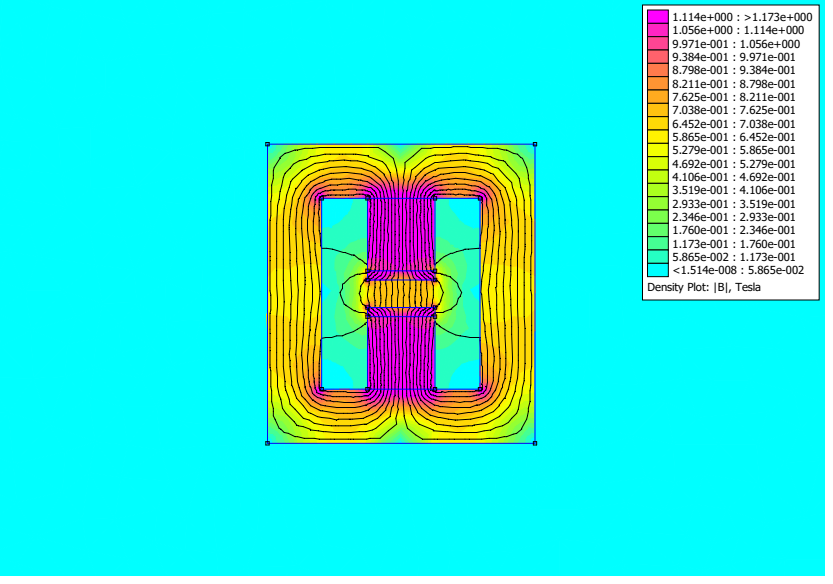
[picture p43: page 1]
Density Plot: |B|, Tesla

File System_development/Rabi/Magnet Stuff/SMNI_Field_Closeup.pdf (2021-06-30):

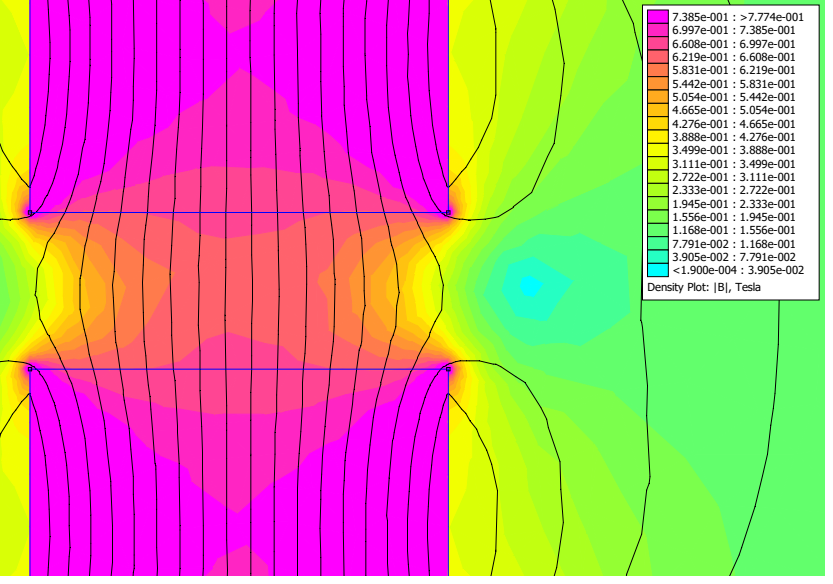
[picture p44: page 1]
Density Plot: |B|, Tesla

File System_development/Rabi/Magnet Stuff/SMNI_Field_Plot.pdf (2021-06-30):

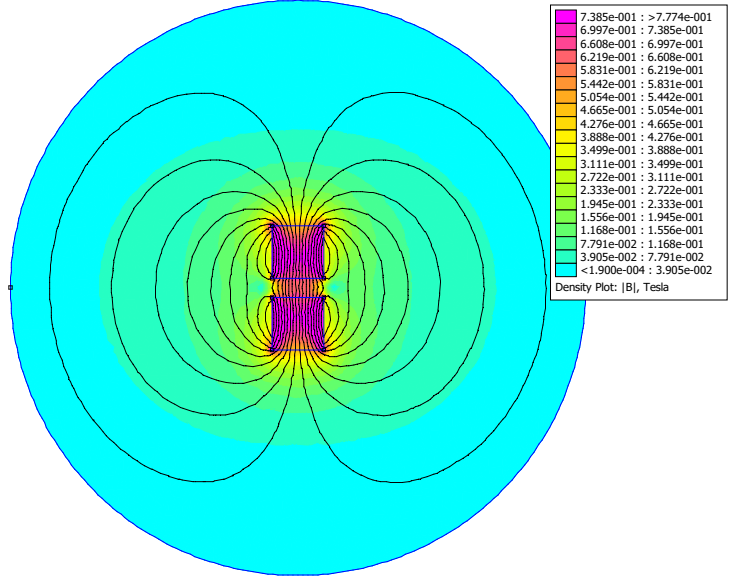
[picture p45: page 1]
Density Plot: |B|, Tesla

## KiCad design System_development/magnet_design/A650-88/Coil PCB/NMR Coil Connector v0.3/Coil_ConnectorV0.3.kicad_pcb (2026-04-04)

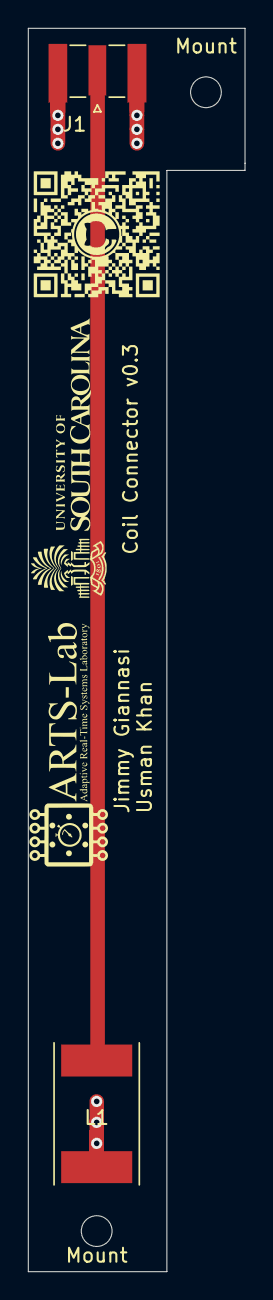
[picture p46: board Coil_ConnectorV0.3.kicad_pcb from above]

Board: 2 copper layers, 15.5 x 88.9 mm, 4 parts (0 on the bottom side), 2 nets.

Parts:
J1: Conn_Coaxial; SMA_Samtec_SMA-J-P-X-ST-EM1_EdgeMount
L1: L; L_Coil
Mount: MountingHole_2.2mm_M2
Mount#2: MountingHole_2.2mm_M2

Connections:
GND: J1.2, L1.2
unnamed: J1.1, L1.1

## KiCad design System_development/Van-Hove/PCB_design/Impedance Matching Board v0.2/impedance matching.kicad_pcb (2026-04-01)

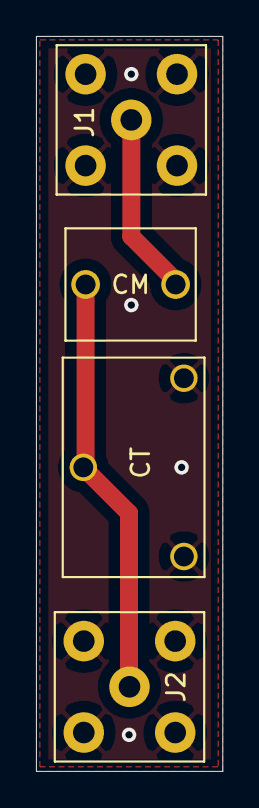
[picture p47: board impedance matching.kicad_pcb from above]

Board: 2 copper layers, 10.4 x 40.8 mm, 4 parts (0 on the bottom side), 3 nets.

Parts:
CM: C_Variable; C_Rect_L7.0mm_W6.0mm_P5.00mm
CT: C_Trim_3_Leg; C_Trim_GZD10100
J1, J2: Conn_Coaxial; SMA_Amphenol_132203-12_Horizontal

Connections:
GND: CT.1, CT.2, J1.2, J2.2
unnamed: CM.1, CT.3, J2.1
unnamed: CM.2, J1.1

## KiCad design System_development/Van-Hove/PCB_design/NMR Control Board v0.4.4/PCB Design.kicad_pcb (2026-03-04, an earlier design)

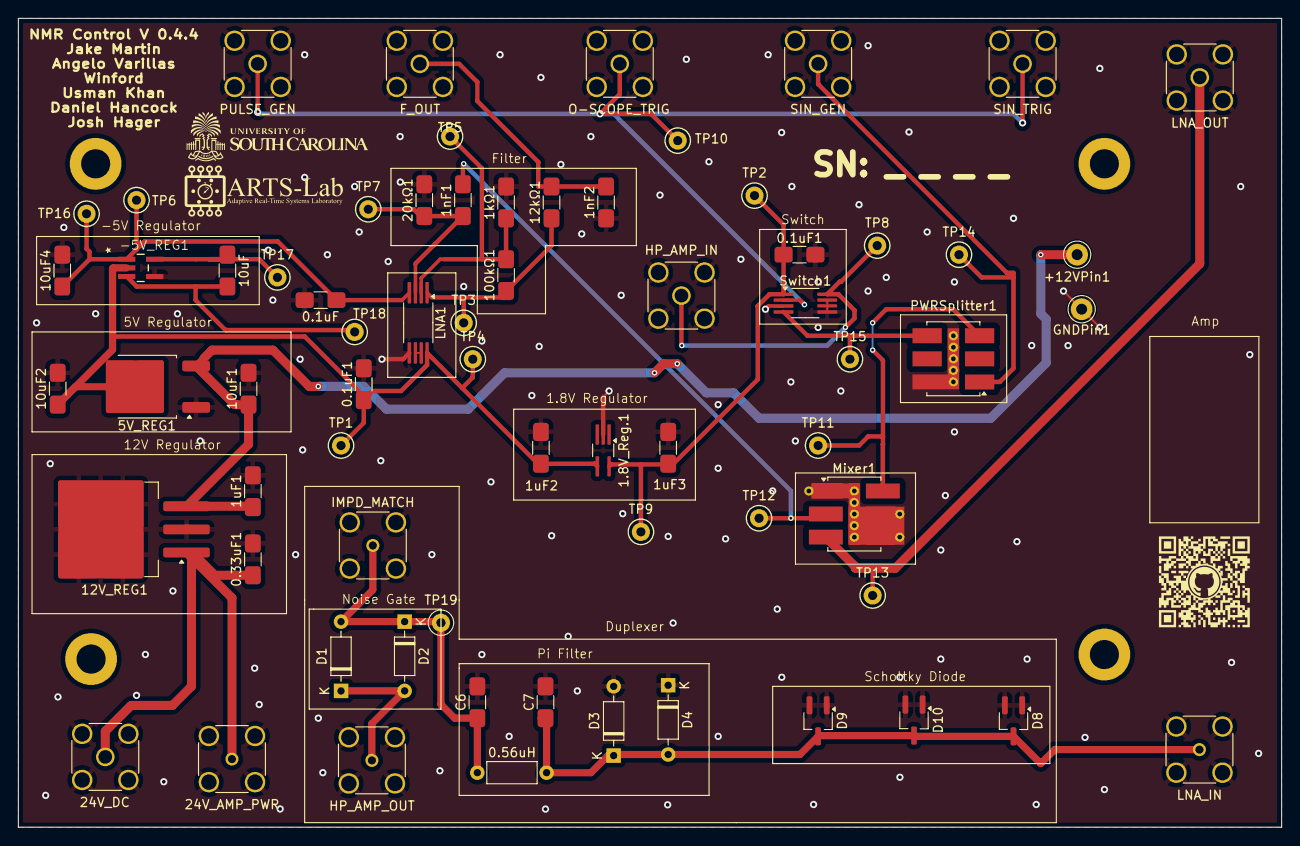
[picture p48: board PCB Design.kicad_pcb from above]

Board: 2 copper layers, 139.0 x 89.0 mm, 68 parts (0 on the bottom side), 23 nets.

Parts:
0.1uF, 0.1uF1, 0.1uF1#2: 0.1μF; CustomR
0.33uF1: 0.33μF; CustomR
0.56uH: L; L_Axial_L5.3mm_D2.2mm_P7.62mm_Horizontal_Vishay_IM-1
1.8V_Reg.1: NCP715-1.8V; 1.8VReg
1kΩ1: 1kΩ; CustomR
1nF1, 1nF2: 1nF; CustomR
1uF1, 1uF2, 1uF3: 1μF; CustomR
5V_REG1: NCP1117-5.0_TO252; 5VReg2
10uF, 10uF1, 10uF2, 10uF4: 10μF; CustomR
12V_REG1: LM7812_TO220; 5VReg
12kΩ1: 12kΩ; CustomR
20kΩ1: 20kΩ; CustomR
24V_AMP_PWR: 24V Amp; SMA_Amphenol_132134-14_Vertical
24V_DC: 24V DC; SMA_Amphenol_132134_Vertical
100kΩ1: 100kΩ; CustomR
+12VPin1: Conn_Coaxial; Pin_D1.0mm_L10.0mm_LooseFit
-5V_REG1: LM828M5; Mf05A
C6: C14; CustomR
C7: C15; CustomR
D1, D2, D3, D4: 1N4148; D_DO-35_SOD27_P7.62mm_Horizontal
D8, D9, D10: D_Schottky_Dual_Series_AKC; TSOT-23_HandSoldering
F_OUT: Output Function; SMA_Amphenol_132134_Vertical
GNDPin1: Conn_Coaxial; Pin_D1.0mm_L10.0mm_LooseFit
HP_AMP_IN: Sine Out; SMA_Amphenol_132134_Vertical
HP_AMP_OUT: Input 1; SMA_Amphenol_132134-14_Vertical
IMPD_MATCH: Imped Match; SMA_Amphenol_132134-14_Vertical
LNA1: LM4565; LNA
LNA_IN: Output; SMA_Amphenol_132134-14_Vertical
LNA_OUT: Mix RF; SMA_Amphenol_132134_Vertical
Mixer1: ADE-6; Mixer2
O-SCOPE_TRIG: Trig Out; SMA_Amphenol_132134_Vertical
PULSE_GEN: Pulse Wave; SMA_Amphenol_132134_Vertical
PWRSplitter1: ADP-2-1W; Mini-Circuits_CD636_LandPatternPL-035
SIN_GEN: SPI In; SMA_Amphenol_132134_Vertical
SIN_TRIG: Sine Wave; SMA_Amphenol_132134_Vertical
Switch1: ADG901BRMZ; Switch
TP1, TP2, TP3, TP4, TP5, TP6, TP7, TP8, TP9, TP10, TP11, TP12, TP13, TP14, TP15, TP16, TP17, TP18, TP19: TestPoint; TestPoint_Keystone_5000-5004_Miniature

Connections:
GND: 0.1uF.2, 0.1uF1.2, 0.1uF1#2.2, 0.33uF1.2, 1.8V_Reg.1.2 (GND), 1kΩ1.2, 1nF2.1, 1uF1.2, 1uF2.2, 1uF3.2, 5V_REG1.1 (GND), 10uF1.2, 10uF2.2, 10uF4.2, 12V_REG1.2 (GND), 20kΩ1.2, 24V_AMP_PWR.2 (Ext), 24V_DC.2 (Ext), -5V_REG1.4 (GND), C6.2, C7.2, D3.2 (A), D4.1 (K), D8.1 (A), D8.2 (K), D9.1 (A), D9.2 (K), D10.1 (A), D10.2 (K), F_OUT.2 (Ext), GNDPin1.1 (In), HP_AMP_IN.2 (Ext), HP_AMP_OUT.2 (Ext), IMPD_MATCH.2 (Ext), LNA1.5 (+IN2), LNA_IN.2 (Ext), LNA_OUT.2 (Ext), Mixer1.1 (GND), Mixer1.4 (GND), Mixer1.5 (GND), O-SCOPE_TRIG.2 (Ext), PULSE_GEN.2 (Ext), PWRSplitter1.6 (GND), SIN_GEN.2 (Ext), SIN_TRIG.2 (Ext), Switch1.3 (GND), Switch1.5 (GND), Switch1.6 (GND), Switch1.7 (GND)
unnamed: 0.1uF1#2.1, 1.8V_Reg.1.5 (OUT), 1uF3.1, Switch1.1 (VDD), TP2.1, TP9.1
unnamed: 0.33uF1.1, 12V_REG1.1 (VI), 24V_AMP_PWR.1 (In), 24V_DC.1 (In)
unnamed: 1uF1.1, 5V_REG1.3 (VI), 10uF1.1, 12V_REG1.3 (VO), +12VPin1.1 (In)
unnamed: 10uF.1, -5V_REG1.5 (C1+), TP17.1
unnamed: 10uF.2, -5V_REG1.3 (C1-), TP18.1
unnamed: 0.1uF.1, 10uF4.1, -5V_REG1.1 (OUT), LNA1.4 (VEE), TP6.1, TP16.1
unnamed: 0.1uF1.1, 1.8V_Reg.1.4 (IN), 1uF2.1, 5V_REG1.2 (VO), 10uF2.1, -5V_REG1.2 (V+), LNA1.8 (VCC), TP1.1, TP4.1
unnamed: 0.56uH.1, C6.1, D1.2 (A), D2.1 (K), IMPD_MATCH.1 (In), TP19.1
unnamed: D1.1 (K), D2.2 (A), HP_AMP_OUT.1 (In)
unnamed: 0.56uH.2, C7.1, D3.1 (K), D4.2 (A), D8.3 (common), D9.3 (common), D10.3 (common), LNA_IN.1 (In)
unnamed: O-SCOPE_TRIG.1 (In), PULSE_GEN.1 (In), SIN_TRIG.1 (In), Switch1.2 (CTRL), TP10.1
unnamed: HP_AMP_IN.1 (In), Switch1.8 (RF2), TP8.1
unnamed: PWRSplitter1.1 (SUM), SIN_GEN.1 (In), TP14.1
unnamed: LNA_OUT.1 (In), Mixer1.3 (RF), TP13.1
unnamed: 1nF2.2, 12kΩ1.2, F_OUT.1 (In)
unnamed: 1nF1.1, 20kΩ1.1, LNA1.3 (+IN1), TP7.1
unnamed: 1kΩ1.1, 100kΩ1.2, LNA1.2 (-IN1), TP5.1
unnamed: LNA1.6 (-IN2), LNA1.7 (OUT2)
unnamed: 12kΩ1.1, 100kΩ1.1, LNA1.1 (OUT1), TP3.1
unnamed: 1nF1.2, Mixer1.2 (IF), TP12.1
unnamed: Mixer1.6 (LO), PWRSplitter1.3 (PORT1), TP11.1
unnamed: PWRSplitter1.4 (PORT2), Switch1.4 (RF1), TP15.1

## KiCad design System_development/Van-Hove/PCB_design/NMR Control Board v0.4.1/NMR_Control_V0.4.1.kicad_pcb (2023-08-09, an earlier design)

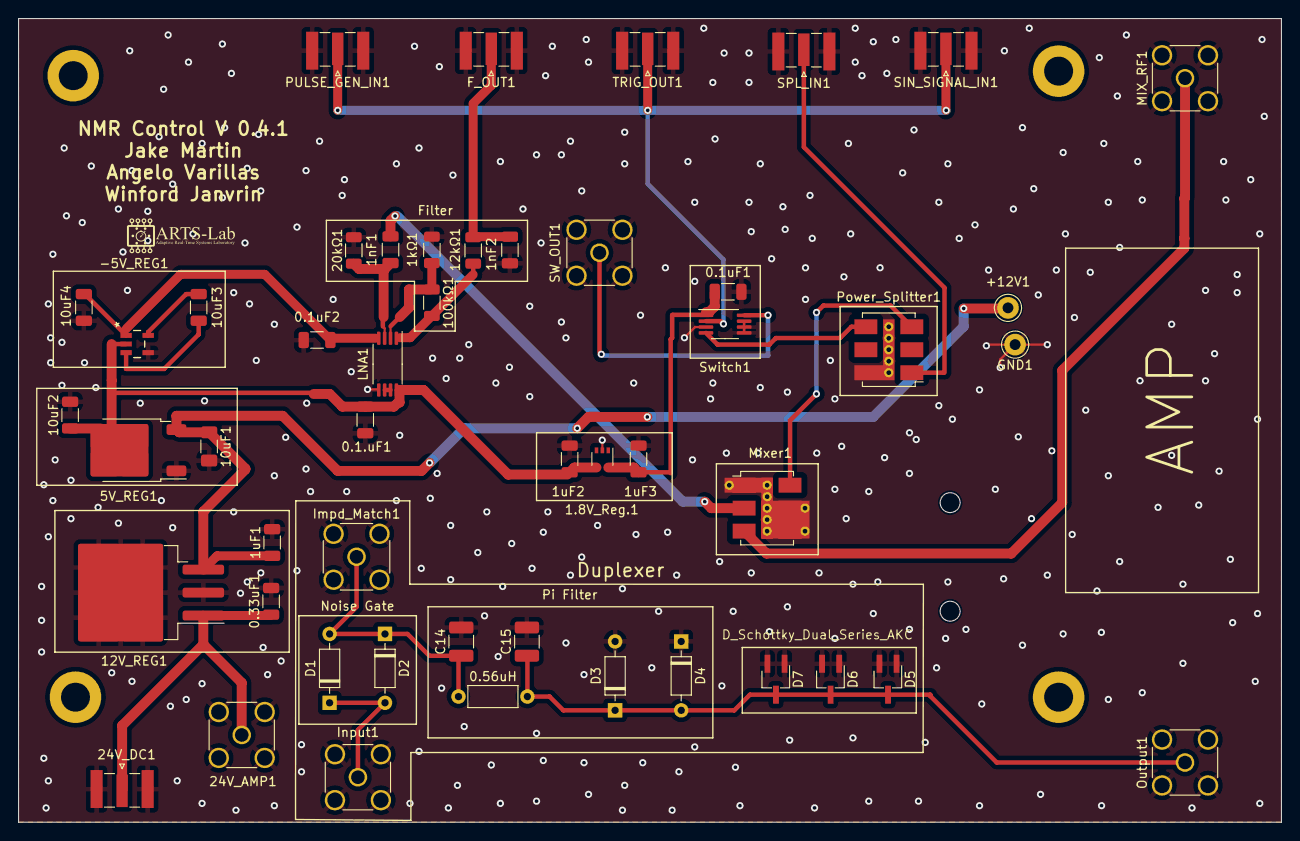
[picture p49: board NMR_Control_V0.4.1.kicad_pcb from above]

Board: 2 copper layers, 139.7 x 88.9 mm, 49 parts (0 on the bottom side), 23 nets.

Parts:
0.1.uF1, 0.1uF2: 0.1uF; C_1206_3216Metric
0.1uF1: 0.1 uF; C_1206_3216Metric
0.33uF1: 0.33 uF; C_1206_3216Metric
0.56uH: L; L_Axial_L5.3mm_D2.2mm_P7.62mm_Horizontal_Vishay_IM-1
1.8V_Reg.1: NCP715-1.8V; SOT-353_SC-70-5
1kΩ1, 12kΩ1, 20kΩ1, 100kΩ1: R; R_1206_3216Metric
1nF1, 1nF2: C; C_1206_3216Metric
1uF1, 1uF2, 1uF3: 1 uF; C_1206_3216Metric
5V_REG1: NCP1117-5.0_TO252; TO-252-2
10uF1: 10 uF; C_1206_3216Metric_Pad1.33x1.80mm_HandSolder
10uF2, 10uF3, 10uF4: 10 uF; C_1206_3216Metric
12V_REG1: LM7812_TO220; TO-263-3_TabPin2
24V_AMP1: Conn_Coaxial; SMA_Amphenol_132291_Vertical
24V_DC1: Conn_Coaxial; SMA_Samtec_SMA-J-P-X-ST-EM1_EdgeMount
+12V1: Pin Hole; Pin_D1.0mm_L10.0mm_LooseFit
-5V_REG1: LM828M5; MF05A
C14, C15: C; C_1210_3225Metric_Pad1.33x2.70mm_HandSolder
D1, D2, D3, D4: 1N4148; D_DO-35_SOD27_P7.62mm_Horizontal
D5, D6, D7: D_Schottky_Dual_Series_AKC; TSOT-23_HandSoldering
F_OUT1: Conn_Coaxial; SMA_Samtec_SMA-J-P-X-ST-EM1_EdgeMount
GND1: Pin Hole; Pin_D1.0mm_L10.0mm_LooseFit
Impd_Match1: Conn_Coaxial; SMA_Amphenol_132134_Vertical
Input1: Conn_Coaxial; SMA_Amphenol_132291_Vertical
LNA1: LM4565; TSSOP-8_4.4x3mm_P0.65mm
MIX_RF1: Conn_Coaxial; SMA_Amphenol_132291_Vertical
Mixer1: ADE-6; Mini-Circuits_CD542_LandPatternPL-052
Output1: Conn_Coaxial; SMA_Amphenol_132291_Vertical
PULSE_GEN_IN1: Conn_Coaxial; SMA_Samtec_SMA-J-P-X-ST-EM1_EdgeMount
Power_Splitter1: ADP-2-1W; Mini-Circuits_CD636_LandPatternPL-035
SIN_SIGNAL_IN1: Conn_Coaxial; SMA_Samtec_SMA-J-P-X-ST-EM1_EdgeMount
SPL_IN1: Conn_Coaxial; SMA_Samtec_SMA-J-P-X-ST-EM1_EdgeMount
SW_OUT1: Conn_Coaxial; SMA_Amphenol_132291_Vertical
Switch1: ADG901BRMZ; MSOP-8_3x3mm_P0.65mm
TRIG_OUT1: Conn_Coaxial; SMA_Samtec_SMA-J-P-X-ST-EM1_EdgeMount

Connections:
GND: 0.1.uF1.1, 0.1uF1.1, 0.1uF2.1, 0.33uF1.2, 1.8V_Reg.1.2 (GND), 1kΩ1.1, 1nF2.1, 1uF1.2, 1uF2.2, 1uF3.2, 5V_REG1.1 (GND), 10uF1.2, 10uF2.2, 10uF4.2, 12V_REG1.2 (GND), 20kΩ1.2, 24V_AMP1.2 (Ext), 24V_DC1.2 (Ext), -5V_REG1.4 (GND), C14.2, C15.2, D3.2 (A), D4.1 (K), D5.1 (A), D5.2 (K), D6.1 (A), D6.2 (K), D7.1 (A), D7.2 (K), F_OUT1.2 (Ext), GND1.1 (In), Impd_Match1.2 (Ext), Input1.2 (Ext), LNA1.5 (+IN2), MIX_RF1.2 (Ext), Mixer1.1 (GND), Mixer1.4 (GND), Mixer1.5 (GND), Output1.2 (Ext), PULSE_GEN_IN1.2 (Ext), Power_Splitter1.6 (GND), SIN_SIGNAL_IN1.2 (Ext), SPL_IN1.2 (Ext), SW_OUT1.2 (Ext), Switch1.3 (GND), Switch1.5 (GND), Switch1.6 (GND), Switch1.7 (GND), TRIG_OUT1.2 (Ext)
unnamed: 0.1uF1.2, 1.8V_Reg.1.5 (OUT), 1uF3.1, Switch1.1 (VDD)
unnamed: 0.33uF1.1, 12V_REG1.1 (VI), 24V_AMP1.1 (In), 24V_DC1.1 (In)
unnamed: 1uF1.1, 5V_REG1.3 (VI), 10uF1.1, 12V_REG1.3 (VO), +12V1.1 (In)
unnamed: 10uF3.1, -5V_REG1.5 (C1+)
unnamed: 10uF3.2, -5V_REG1.3 (C1-)
unnamed: 0.1uF2.2, 10uF4.1, -5V_REG1.1 (OUT), LNA1.4 (VEE)
unnamed: 0.1.uF1.2, 1.8V_Reg.1.4 (IN), 1uF2.1, 5V_REG1.2 (VO), 10uF2.1, -5V_REG1.2 (V+), LNA1.8 (VCC)
unnamed: 0.56uH.1, C14.1, D1.2 (A), D2.1 (K), Impd_Match1.1 (In)
unnamed: D1.1 (K), D2.2 (A), Input1.1 (In)
unnamed: 0.56uH.2, C15.1, D3.1 (K), D4.2 (A), D5.3 (common), D6.3 (common), D7.3 (common), Output1.1 (In)
unnamed: 1nF2.2, 12kΩ1.2, F_OUT1.1 (In)
unnamed: 1nF1.1, 20kΩ1.1, LNA1.3 (+IN1)
unnamed: 1kΩ1.2, 100kΩ1.1, LNA1.2 (-IN1)
unnamed: LNA1.6 (-IN2), LNA1.7 (OUT2)
unnamed: 12kΩ1.1, 100kΩ1.2, LNA1.1 (OUT1)
unnamed: MIX_RF1.1 (In), Mixer1.3 (RF)
unnamed: 1nF1.2, Mixer1.2 (IF)
unnamed: Mixer1.6 (LO), Power_Splitter1.3 (PORT1)
unnamed: PULSE_GEN_IN1.1 (In), SIN_SIGNAL_IN1.1 (In), Switch1.2 (CTRL), TRIG_OUT1.1 (In)
unnamed: Power_Splitter1.4 (PORT2), Switch1.4 (RF1)
unnamed: Power_Splitter1.1 (SUM), SPL_IN1.1 (In)
unnamed: SW_OUT1.1 (In), Switch1.8 (RF2)

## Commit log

2020-10-06 Diode Gate version 1
    [Diode_Gate_2-B_Cu.gbl, Diode_Gate_2-B_Mask.gbs, Diode_Gate_2-B_SilkS.gbo, Diode_Gate_2-Edge_Cuts.gm1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]
2020-10-06 Uploaded Diode Gate 1
    [Diode_Gate_1.kicad_pcb, Diode_Gate_1.sch, Diode_Gate_2-B_Cu.gbl, Diode_Gate_2-B_Mask.gbs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]
2020-10-07 Diode Gate 3
    [Diode_Gate_1.kicad_pcb, Diode_Gate_2.kicad_pcb, Diode_Gate_3.kicad_pcb, Diode_Gate_3.sch]
2020-10-07 added text, testing push
    [Diode_Gate_1.kicad_pcb, Diode_Gate_2.kicad_pcb, Diode_Gate_3.kicad_pcb]
2020-10-24 Probe Board v2.0 was finished and uploaded
    [Probe_Board_v2.0.kicad_pcb, Probe_Board_v2.0.sch]
2021-06-30 Magnet Simulations & Case Files
    [TWO MAG BODY 1.5x1.5 v3.f3d, TWO MAG BODY 1.5x1.5 v3.obj, TWO MAG BODY 3x1 v13.f3d]
2021-06-30 Magnet strength mapping
    [Halbach Magnet Mapping.xlsx, Large Magnet Mapping.xlsx, Small Magnet Mapping.xlsx]
2021-07-01 updated layout
    [Diode_Gate_1.kicad_pcb, Diode_Gate_1.sch, Diode_Gate_2.kicad_pcb, Diode_Gate_2.sch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]
2021-07-01 First PCB design for housing surface mount components
    [NMR_Control_1.kicad_pcb, NMR_Control_1.sch]
2021-07-07 Magnet & Tray 3D Print Files
    [TRAY 3x1 v11.f3d, TRAY 3x1 v12.f3d, TWO MAG BODY 1.5x1.5 v3.f3d, TWO MAG BODY 1.5x1.5 v3.obj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]
2021-08-16 Large update to V1 & V2 folders
    Updated and added several folders
    [Main_PCB_V2.kicad_pcb, Main_PCB_V2.sch, NMR_Control_1.kicad_pcb, Pi_Filter_V1.kicad_pcb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]
2021-08-17 pcb file cleanup
    [Main_PCB_V2.kicad_pcb, Main_PCB_V2.sch, Probe_Matching_Board_V2.kicad_pcb, Probe_Matching_Board_V2.sch]
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2021-11-10 C-NMR LN Amplifier PCB
    Created a PCB design for the low noise amplifier chain needed for test carbon NMR
    [CNMR_LN_Amplifiers_V1.kicad_pcb, CNMR_LN_Amplifiers_V1.sch]
2021-11-12 MATLAB & KiCad edits
    [CNMR_LN_Amplifiers_V1.kicad_pcb]
2021-12-07 Code changes
    [CNMR_LN_Amplifiers_V1.kicad_pcb, Lowpass Filter & Amp.kicad_pcb, Lowpass Filter & Amp.sch, Main_PCB_V2.kicad_pcb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]
2021-12-10 ASTM Documents
    Added ASTM NMR documents and moved the 5mm sample tube holder into the 3D print files folder in V2
    [Hole Ends NMR.stl, Holes NMR.stl, Side Support NMR.stl]
2021-12-10 Create TRAY 3x1 v12.f3d
    [TRAY 3x1 v12.f3d]
2022-01-26 Create block v4.f3d
    [block v4.f3d]
2022-01-26 Update block v4.f3d
    [block v4.f3d]
2022-02-02 Reorganized some files/folders
    Added some magnet files and renamed a few folders
    [CNMR_LN_Amplifiers_V1.kicad_pcb, CNMR_LN_Amplifiers_V1.sch, Diode_Gate_1.kicad_pcb, Diode_Gate_1.sch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]
2022-02-07 Coil PCB
    Added small PCB used for connecting the coil to SMA cable. This is the only PCB in the sample tray
    [Coil_Connector.kicad_pcb, Coil_Connector.sch]
2022-02-08 Coil Connector PCB
    Added screw holes
    [Coil_Connector.kicad_pcb, HP_Amplifier_Test_Board.kicad_pcb, HP_Amplifier_Test_Board.kicad_sch]
2022-02-09 update 9Feb2022
    [TRAY 3x1.5 v4.f3d, TWO MAG BODY 3x1.5 v01.f3d]
2022-02-10 PCB updates
    [HP_Amplifier_Test_Board.kicad_sch, Large Magnet Mapping.xlsx]
2022-02-16 Coil PCB & HP Amp PCB
    [Coil_Connector.kicad_pcb, Coil_Connector.kicad_sch, Coil_Connector.sch, HP_Amplifier_Test_Board.kicad_pcb]
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2022-04-06 General updates
    PCBs & Matlab processing edits
    [Coil_Connector.kicad_pcb, Main_PCB_V3.kicad_pcb, Main_PCB_V3.kicad_sch, Main_PCB_V3.sch]
2022-04-15 LabVIEW & moved some files
    Updated LabVIEW T2 testing code, and the MATLAB post-processing code
    [tuberackbase.stl, tuberackrings2.stl, tuberackside.stl]
2022-04-15 update 4/15/22
    [Mag Body 3x1.5 V02 v1.f3d, TRAY 3x1.5 V02 v6.f3d, TRAY 3x1.5 V03 v1.f3d, TRAY 3x1.5 v01.1 v3.f3d]
2022-04-15 cleaned up reop
    [CNMR_LN_Amplifiers_V1.kicad_pcb, CNMR_LN_Amplifiers_V1.sch, Coil_Connector.kicad_pcb, Coil_Connector.kicad_sch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]
2022-04-25 Create MagBody 3x1.5 V02 v1.f3d
    [MagBody 3x1.5 V02 v1.f3d]
2022-05-27 New PCB versions
    - Main board (RF routing) V3
    - Regulator board (24V to 12V, 5V, 1,8V)
    - HP Amplifier board V2
    [HP_Amplifier_Test_Board.kicad_pcb, HP_Amplifier_Test_Board.kicad_sch, HP_Amplifier_Test_Board_v2.kicad_pcb, HP_Amplifier_Test_Board_v2.kicad_sch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]
2022-05-31 Magnet & PCB stuff
    [CNMR_LN_Amplifiers_V1.kicad_pcb, CNMR_LN_Amplifiers_V1.sch, Coil_Connector.kicad_pcb, Coil_Connector.kicad_sch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]
2022-06-30 New PCB files
    [Lowpass Filter & Amp V2.kicad_pcb, Lowpass Filter & Amp V2.kicad_sch, NMR_control_board_V4.kicad_pcb, NMR_control_board_V4.kicad_sch]
2022-07-12 File cleanup
    Renamed the version numbers, cleaned up duplicates & unnecessary files, and added some recent files.
    [CNMR_LN_Amplifiers_V1.kicad_pcb, CNMR_LN_Amplifiers_V1.sch, Coil_Connector.kicad_pcb, Coil_Connector.kicad_sch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]
2022-09-16 KiCad files
    Removed an unused PCB file and added the new control board PCB to the v0.3 folder (embedded controller system).
    [HP_Amplifier_Test_Board.kicad_pcb, HP_Amplifier_Test_Board.kicad_sch, NMR_control_board_V4.csv, NMR_control_board_V4.kicad_pcb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]
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2023-02-22 PCB
    added schottky diode board
    [Schottky_Diodes.kicad_pcb, Schottky_Diodes.kicad_sch]
2023-02-24 Added V2 of coil pbc and voltage regulation pcb
    [Coil_Connector.kicad_pcb, Coil_Connector_V1.kicad_pcb, Coil_Connector_V1.kicad_sch, Coil_Connector_V2.kicad_pcb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]
2023-04-03 V0.3.2 Control Board
    Includes connections to pulse generator and sin generator and includes labels
    [NMR_control_board_V0.3.2.csv, NMR_control_board_V0.3.2.kicad_pcb, NMR_control_board_V0.3.2.kicad_sch]
2023-04-04 pcb name updates
    [NMR_control_board_V0.3.1.csv, NMR_control_board_V0.3.1.kicad_pcb, NMR_control_board_V0.3.1.kicad_sch]
2023-04-06 kicad files
    [Coil_Connector_V2.kicad_pcb, Coil_Connector_V3_selfprint-B_Cu.gbr, Coil_Connector_V3_selfprint-B_Mask.gbr, Coil_Connector_V3_selfprint-B_Paste.gbr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]
2023-04-06 Kicad and pulse train files
    [NMR_control_board_V0.3.2-B_Cu.gbr, NMR_control_board_V0.3.2-B_Mask.gbr, NMR_control_board_V0.3.2-B_Paste.gbr, NMR_control_board_V0.3.2-B_Silkscreen.gbr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]
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2023-05-15 File name updates (v0.1)
    [NMR diode noise gate - v0.1.1.kicad_pcb, NMR diode noise gate - v0.1.1.sch, NMR diode noise gate - v0.1.2.kicad_pcb, NMR diode noise gate - v0.1.2.sch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]
2023-06-19 3d print file for small NMR magnet
    [Small Square Magnet Holder v3.f3d]
2023-06-20 PCB updates including Control Board V0.3.2 and Voltage regulator V0.3.2 and V0.3.3
    [NMR_control_board_V0.3.2.kicad_pcb, Voltage_Regulator_v0.3.2.kicad_pcb, Voltage_Regulator_v0.3.2.kicad_sch, Voltage_Regulator_v0.3.3.kicad_pcb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]
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2023-06-21 File organization for 3D print files
    [Mag Body 3x1.5 V02 v1.f3d, MagBody 3x1.5 V02 v1.f3d, Small Magnet tray v0.3.2.f3d, Small Magnet tray v0.3.2.step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]
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2023-08-08 NMR Control Board V 0.4.1
    uploaded NMR Control Board V 0.4.1
    [NMR main Board.kicad_pcb, NMR main Board.kicad_sch]
2023-08-09 Updated the NMR Board
    No warning on the board, looks good order
    [NMR main Board.kicad_pcb]
2023-08-09 Control Board 0.4.1 adjustments
    [NMR_Control_V0.4.1.kicad_pcb, NMR_Control_V0.4.1.kicad_sch]
2023-08-09 PCV v0.4.1 edits
    Just removed/edited some vias and also changed the track width for a few traces.
    [NMR_Control_V0.4.1 - edited.kicad_pcb, NMR_Control_V0.4.1 - edited.kicad_sch]
2023-08-09 Port name edits
    [NMR_Control_V0.4.1 - edited.kicad_pcb]
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2024-01-26 Added pulse sequences for the small magnet setup with the PE15A4017 amp
    [NMR_Control_V0.4.1 - edited.kicad_pcb]
2024-02-19 New tray design and File organization
    [Coil_Connector_V2.kicad_pcb, Probe_Matching_Board_V2.kicad_pcb, Probe_Matching_Board_V2.kicad_sch, Small Magnet tray v0.4.2.f3d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]
2024-02-26 NMR Control Board v0.5
    Compact PCB design of NMR Control Board v0.4
    [NMR Control Board V 0.5.kicad_pcb, NMR Control Board V 0.5.kicad_sch]
2024-02-29 Edit NMR Control v0.5
    Added two SMA connectors to RF switch input.
    [NMR Control Board V 0.5.kicad_pcb, NMR Control Board V 0.5.kicad_sch]
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2024-07-31 Removing design updates under wrong account name
    [b645_case v0.1.stl, b645_case v0.1.stp]
2024-07-31 Adding b645 case designs (this time under the correct account and not my personal one)
    [b645_case v0.1.stl, b645_case v0.1.stp]
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2025-05-30 Fixed V 0.4.3's issue with the mixer pad's, github's QR code, added the USC logo and adjusted the sizing of the ARTS logo, and the sizing/location of certain component names and pads, and added a pla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
    [PCB Design-B_Cu.gbr, PCB Design-B_Mask.gbr, PCB Design-B_Paste.gbr, PCB Design-B_Silkscreen.gbr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]
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2026-03-24 Updated Magnet Assembly Support
    Updated Magnet Assembly supports 6x5x10 and 6x7x10 to fit the correct dimensions.
    [Assembly_6x5x10.stp, Assembly_6x6x10.stp]
2026-03-24 Updated Magnet Assembly Supports
    Updated the Magnet Assembly supports to fit correct dimensions.
    [Assembly_6x6x10.stp, Assembly_6x7x10.stp]
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2026-04-01 fixed version number spacing, adding logos/QR code to coil connector.
    [Coil_Connector.kicad_pcb, Coil_Connector.kicad_sch, Coil_ConnectorV0.3.kicad_pcb, Coil_ConnectorV0.3.kicad_sch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]
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
